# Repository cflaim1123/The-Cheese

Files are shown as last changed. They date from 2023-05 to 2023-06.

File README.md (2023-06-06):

# The-Cheese
This repository documents the design and construction of a sensor that measures changes in water clarity due to wave action.

The water clarity sensor uses image recognition analysis of ball markers at known distances from the camera to calculate visibility distance in a water column. The sensor takes pressure readings at 5 Hz and takes an image to be analyzed every 100 pressure samples. The goal of the sensor is to correlate water clarity and suspended sediment concentrations to wave intensity in coastal environments. Water clarity can impact benthic organisms who rely on visible water to navigate and hunt. Additionally, cloudy water attenuates light more quickly and can reduce primary production rates in coastal photosynthesizing organisms.

Project summary:
A current study was carried out to provide a better understanding of the effects of wave intensity on suspended sediment concentrations in coastal environments. Sediment grain disruptions, generally caused by boat traffic, increase the mortality rates of species and disrupt photosynthesis. Studying sediment disturbances alongside wave energy is important for determining possible commercial and recreational regulations surrounding marine environments. While utilizing our designed and built sensor, we predict that as the measured wave intensity increases in Puget Sound, the measured suspended sediment concentration increase as well. This is due to increased wave energy resulting in increased sediment transport based on the grain size and magnitude of the wave intensity. With our sensor, we will measure the presence of a wave through pressure readings and shifts in suspended sediment concentrations with digital camera imagery. The instrument will take a picture and readings across the pressure sensor to sense the amount of suspended sediment stirred up with the occurrence of a wave. We experienced challenges across all aspects of the instrument design; from the initially considered components and appearance to the coding process and marker programming. The sensor’s deployment site is the Mukilteo T Dock chosen for its diversity in sediment grain size and isolated location. The date for our deployment is during Memorial Day weekend; a convenient holiday associated with heavy boat traffic and recreational wave energy. Eventually, through a familiar cycle of trial and error, we were able to achieve a functional sensor known to us as The Cheese.

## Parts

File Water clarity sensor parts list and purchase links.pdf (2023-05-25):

Water clarity sensor parts list and purchase links Electronics
- Adafruit ESP32-s2 feather BME (https://www.adafruit.com/product/5303)
- AIthinker ESP32-cam (https://www.amazon.com/ESP32-CAM-MB-Aideepen-ESP32-CAM-Bluetooth-Arduino/dp/B0948ZFTQZ)
- MS5803BA_05 pressure sensor (https://www.digikey.com/en/products/detail/te-connectivity-measurement-specialties/MS580314BA01-00/5277631) on 4-pint (+3V, -3V, SDA, SCL) breakout board
- DS3231 real time clock (RTC) (https://www.amazon.com/HiLetgo-AT24C32-Arduino-Without-Battery/dp/B00LX3V7F0?hvadid=312400581241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)
- DF robot SD card module (https://www.digikey.com/en/products/detail/dfrobot/DFR0229/6588460)
- 6-pin switch (https://www.digikey.com/en/products/detail/c&k/JS202011CQN/1640097)
- 9V battery (x2) (https://www.amazon.com/AmazonBasics-Volt-Everyday-Alkaline-Battery/dp/B081FGCRQQ?hvadid=177774793098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)
- 9V battery lead wires (x2) (https://www.amazon.com/Chanzon-Battery-Connector-Plastic-Arduino/dp/B083QF1KHN)
- Female header mounts (https://www.amazon.com/Cimeton-Electrical-Connectors-Assortment-Prototype/dp/B09B92JPD3)
- Double-sided perf board (https://www.amazon.com/DEYUE-Double-sided-Prototyping-Solder-able-Protoboards/dp/B07FFDFLZ3?s=industrial)
- Multi-colored breadboard wires (https://www.amazon.com/TUOFENG-Hookup-Wires-6-Different-Colored/dp/B07TX6BX47?s=industrial)

Hardware
- Waterproof housing (https://www.polycase.com/ml-46f)
- M3 bolts (x2) (https://www.amazon.com/Assortment-Stainless-Replacement-Machine-Fastener/dp/B0BMQFHDBH?s=industrial)
- M3 lock nuts (x2) (https://www.amazon.com/100Pcs-Stainless-Self-Lock-Inserted-Clinching/dp/B075ZZW7VL?s=industrial)
- Bricks (~5 pounds) (x6) (https://www.homedepot.com/p/Basalite-8-in-x-4-in-x-2-in-Concrete-HW-Brick-Natural-100015626/316606769)
- 12” zip ties (x24) (https://www.amazon.com/White-Strength-Nylon-Bolt-Dropper/dp/B06X1CKSD2?s=industrial)
- 6” zip ties (https://www.amazon.com/KOOWIN-Small-Nylon-Plastic-Cable/dp/B08HMPBY3L?s=industrial)
- ½” plywood (~2 sq. ft) (https://www.homedepot.com/p/Handprint-Sanded-Plywood-Common-1-2-in-x-2-ft-x-4-ft-Actual-0-451-in-x-23-75-in-x-47-75-in-300896/202093833)
- 0.84” OD PVC pipe (1/2” ID) (~5m) (https://www.homedepot.com/p/Charlotte-Pipe-1-in-x-10-ft-PVC-Schedule-40-Tubing-DWV-Pipe-PVC040100600RS/100348473)
- 60° elbow connectors (x6, see project GitHub) (https://github.com/cflaim1123/The-Cheese)
- 90° elbow connectors (x8, see project GitHub) (https://github.com/cflaim1123/The-Cheese)
- Ball distance markers (x14, see project GitHub) (https://github.com/cflaim1123/The-Cheese)
- 1mm wire (~1m) (https://www.amazon.com/Hillman-Group-123106-Galvanized-Steel/dp/B000BPEQAE?hvadid=631557517645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)

Filament
- ABS filament (any color, ~1/4 spool) (https://www.amazon.com/HATCHBOX-3D-Filament-Dimensional-Accuracy/dp/B00MEZEAZ0?s=industrial)

Sealants
- Marine sealant 5200 (https://www.amazon.com/3M-5200FC-Marine-Adhesive-Sealant/dp/B003E1ULRE)
- Hot glue

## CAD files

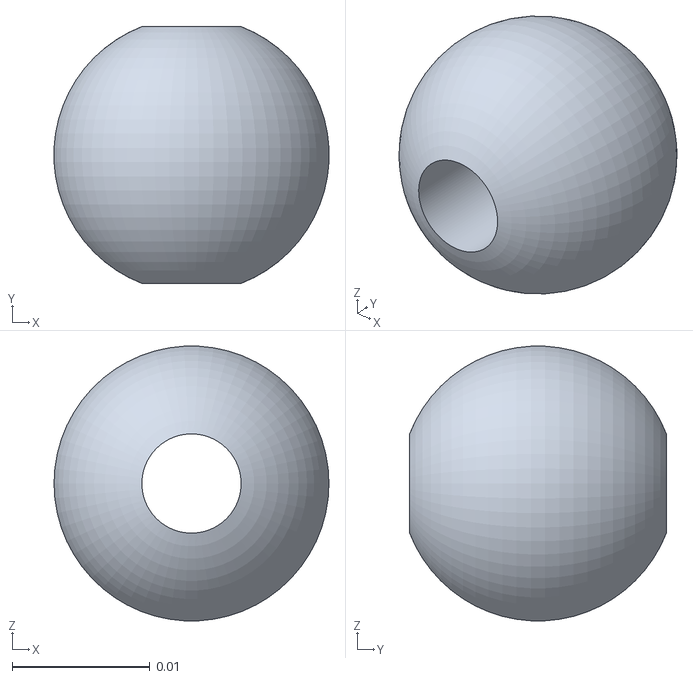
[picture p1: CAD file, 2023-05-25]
STL FILES/ballMarker.stl
0.02 x 0.0187 x 0.0199

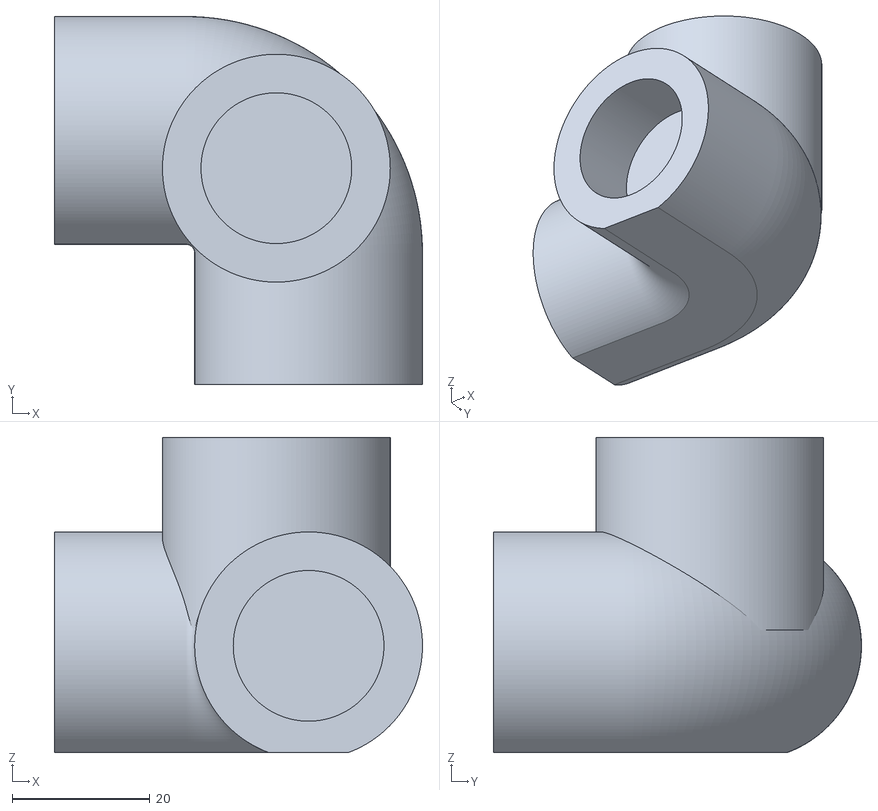
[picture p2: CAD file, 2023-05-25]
STL FILES/90deg0_84InchElbow.stl
53.3 x 53.3 x 45.7

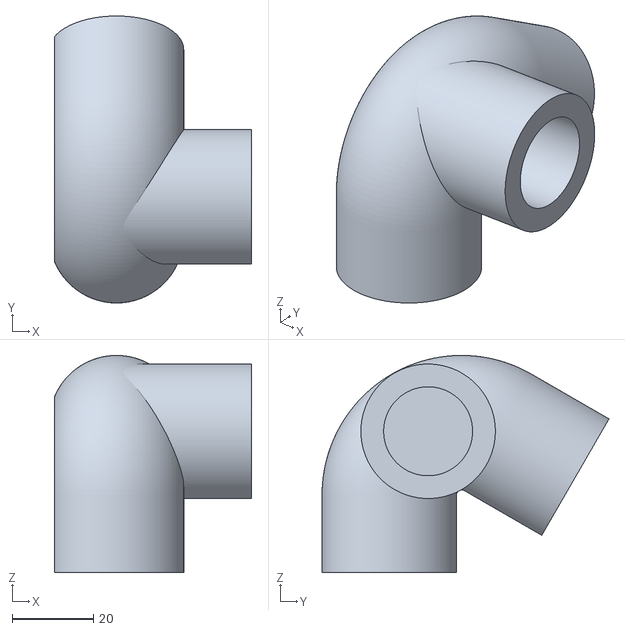
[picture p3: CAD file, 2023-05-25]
STL FILES/60Deg0_84InchElbow.stl
48.4 x 70.5 x 53.3

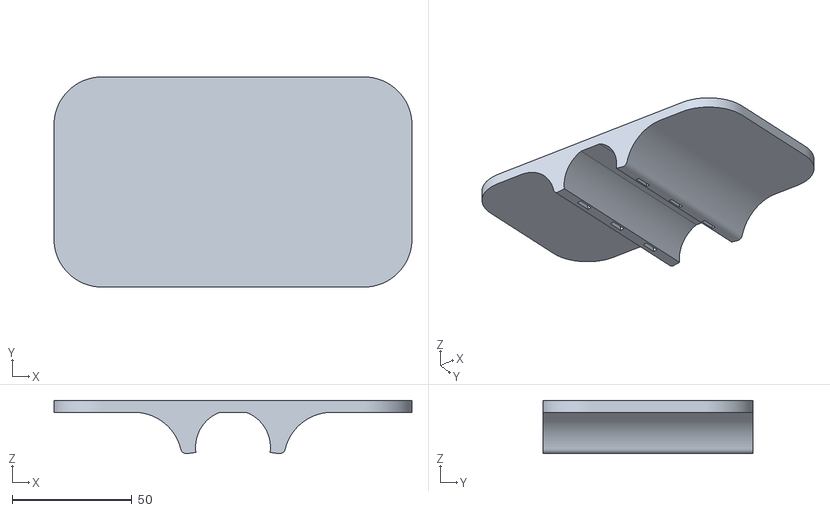
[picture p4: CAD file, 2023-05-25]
STL FILES/waterClaritySensorPipeMountV3.stl
149.3 x 87.6 x 22.2

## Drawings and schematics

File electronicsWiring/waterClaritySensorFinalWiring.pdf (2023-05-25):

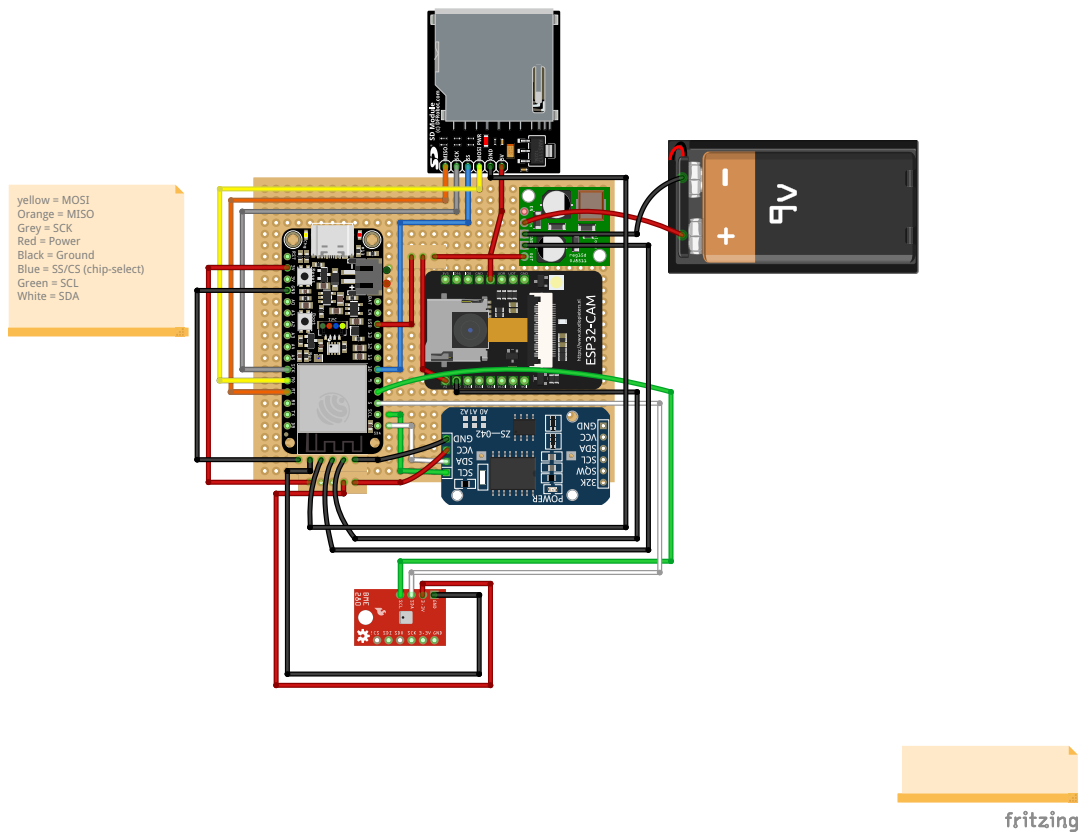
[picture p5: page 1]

yellow = MOSI
Orange = MISO
Grey = SCK
Red = Power
Black = Ground
Blue = SS/CS (chip-select)
Green = SCL
White = SDA

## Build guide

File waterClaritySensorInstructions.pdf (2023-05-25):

Water clarity sensor user instructions
1) Ensure the two 9v batteries beneath the main electronics board are near a full charge.
2) Remove the camera module and then press the SD card to remove it. Delete any photos previously saved to it. Insert the SD card back into the camera module and replace the camera into the female header pins.
3) Pull up an online clock (https://clock.zone/) with millisecond accuracy. Be prepared to take a screenshot of the time while simultaneously turning on the sensor.
4) Locate the power switch in the upper right-hand corner. Pull the switch down (towards the red wire beneath the board) at the same time as taking a screenshot of the current time. You should now see red and orange LEDs on the board.
5) House the battery pack beneath the main board and gently press the main electronics board into place. The stand-offs on the bottom should sit on either side of the two batteries. Note: the batteries will curve slightly inward due to the shape of the housing.
6) Make sure all wires are clear of the O-ring lip prior to sealing the lid onto the housing. Make sure now wires are visibility broken.
7) Gently clean the lid of the pressure casing with methanol or rubbing alcohol.
8) Place the lid onto the pressure housing and begin the tight the four corner screws in a star-like pattern. Once all the screws are loosely in place, fully tighten them. You should still see the LEDs on the board to be powered on.
9) Ensure that the screws are fully tightened and there are no gaps between the lid and pressure housing.
10) Tightly wrap 2 – 4 layers of electrical tape around the seal between the lid and pressure housing. Be sure to overlap the layers so that the tape covers ~1inch in width.
11) Firmly run your fingers over the electrical tape to ensure it has adhered to the pressure vessel.
12) Snap the sealed pressure casing the vertical leg of The Cheese beneath the mounted pressure sensor. Locate three ~6” zip ties.
13) Slide the zip ties through the holes on the back of the pipe mount piece and firmly tighten them so that the pressure housing does not easily rotate.
14) Orient the camera in the pressure housing so that it is aligned with the ball markers.
15) Carry the water clarity sensor to the sampling location along with a flotation device for surface expression. Tie the buoy to the sensor frame upon arrival.
16) Gently lower the sensor into the water and leave submerged for the desired sampling time.
17) To retrieve data from the sensor, unseal the pressure casing (follow steps 11 – 8 in reverse order) and remove the camera SD card. If there is no data on this SD card, check the backup SD card on the bottom side of the main electronics board.

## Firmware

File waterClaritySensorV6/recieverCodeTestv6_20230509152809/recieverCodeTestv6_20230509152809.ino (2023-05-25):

// Include Required Libraries
// Camera libraries
#include "esp_camera.h"
#include "soc/soc.h"
#include "soc/rtc_cntl_reg.h"
#include "driver/rtc_io.h"
// MicroSD Libraries
#include "FS.h"
#include "SD_MMC.h"
// Data transmission libraries
#include <esp_now.h>
#include <WiFi.h>

// Pin definitions for CAMERA_MODEL_AI_THINKER
#define PWDN_GPIO_NUM     32
#define RESET_GPIO_NUM    -1
#define XCLK_GPIO_NUM      0
#define SIOD_GPIO_NUM     26
#define SIOC_GPIO_NUM     27
#define Y9_GPIO_NUM       35
#define Y8_GPIO_NUM       34
#define Y7_GPIO_NUM       39
#define Y6_GPIO_NUM       36
#define Y5_GPIO_NUM       21
#define Y4_GPIO_NUM       19
#define Y3_GPIO_NUM       18
#define Y2_GPIO_NUM        5
#define VSYNC_GPIO_NUM    25
#define HREF_GPIO_NUM     23
#define PCLK_GPIO_NUM     22

// MAC Address of responder - edit as required
uint8_t broadcastAddress[] = {0x84, 0xF7, 0x03, 0xEC, 0xE5, 0x66};

typedef struct struct_message {
  char a[32];
  int b;
  float c;
  float d;
  bool e;
  unsigned long f;
} struct_message;

// Create a structured object
struct_message sensorData;

// Data file 
File dataFile;
const char fileName[] = "/data.csv";

// Counter for picture number
unsigned int pictureCount = 0;
// Delay time in millieconds
unsigned int delayTime = 2020;

// Callback function executed when data is received
void OnDataRecv(const uint8_t * mac, const uint8_t *incomingData, int len) {
  memcpy(&sensorData, incomingData, sizeof(sensorData));
  Serial.print("Data received: ");
  Serial.println(len);
  Serial.print("Time: ");
  Serial.println(sensorData.a);
  Serial.print("Sample num: ");
  Serial.println(sensorData.b);
  Serial.print("Pressure: ");
  Serial.println(sensorData.c);
  Serial.print("Temp: ");
  Serial.println(sensorData.d);
  Serial.print("Picture flag:");
  Serial.println(sensorData.e);
  Serial.print("Elapsed time: ");
  Serial.println(sensorData.f);
  Serial.println();

  String tempDataRow = String(sensorData.b) + "," + String(sensorData.c) + "," + sensorData.d + 
  "," + String(sensorData.a) + "," + String(sensorData.e) + "," + String(sensorData.f);
  const char* dataRow = tempDataRow.c_str();
  appendFile(SD_MMC, "/data.csv",dataRow);

  // Take and Save Photo
  if(sensorData.e == true){
    // Path where new image will be saved in MicroSD card
    String path = "/image_" + String(sensorData.b) +  ".jpg";
    Serial.printf("Picture file name: %s\n", path.c_str());
    takeNewPhoto(path);
  }
}
void appendFile(fs::FS &fs, const char * path, const char * message){
    Serial.printf("Appending to file: %s\n", path);

    File file = fs.open(path, FILE_APPEND);
    if(!file){
        Serial.println("Failed to open file for appending");
        return;
    }
    if(file.println(message)){
        Serial.println("Message appended");
    } else {
        Serial.println("Append failed");
    }
}

void configESPCamera() {
// Configure Camera parameters
// Object to store the camera configuration parameters
camera_config_t config;
config.ledc_channel = LEDC_CHANNEL_0;
config.ledc_timer = LEDC_TIMER_0;
config.pin_d0 = Y2_GPIO_NUM;
config.pin_d1 = Y3_GPIO_NUM;
config.pin_d2 = Y4_GPIO_NUM;
config.pin_d3 = Y5_GPIO_NUM;
config.pin_d4 = Y6_GPIO_NUM;
config.pin_d5 = Y7_GPIO_NUM;
config.pin_d6 = Y8_GPIO_NUM;
config.pin_d7 = Y9_GPIO_NUM;
config.pin_xclk = XCLK_GPIO_NUM;
config.pin_pclk = PCLK_GPIO_NUM;
config.pin_vsync = VSYNC_GPIO_NUM;
config.pin_href = HREF_GPIO_NUM;
config.pin_sscb_sda = SIOD_GPIO_NUM;
config.pin_sscb_scl = SIOC_GPIO_NUM;
config.pin_pwdn = PWDN_GPIO_NUM;
config.pin_reset = RESET_GPIO_NUM;
config.xclk_freq_hz = 20000000;
config.pixel_format = PIXFORMAT_JPEG; // Choices are YUV422, GRAYSCALE, RGB565, JPEG
// Select lower framesize if the camera doesn't support PSRAM
if (psramFound()) {
  config.frame_size = FRAMESIZE_VGA; // FRAMESIZE_ + QVGA|CIF|VGA|SVGA|XGA|SXGA|UXGA
  config.jpeg_quality = 10; //10-63 lower number means higher quality
  config.fb_count = 2;
} else {
  config.frame_size = FRAMESIZE_SVGA;
  config.jpeg_quality = 12;
  config.fb_count = 1;
}
// Initialize the Camera
esp_err_t err = esp_camera_init(&config);
if (err != ESP_OK) {
  Serial.printf("Camera init failed with error 0x%x", err);
  return;
}
// Camera quality adjustments
sensor_t * s = esp_camera_sensor_get();
// BRIGHTNESS (-2 to 2)
s->set_brightness(s, 1);
// CONTRAST (-2 to 2)
s->set_contrast(s, 0);
// SATURATION (-2 to 2)
s->set_saturation(s, 0);
// SPECIAL EFFECTS (0 - No Effect, 1 - Negative, 2 - Grayscale, 3 - Red Tint, 4 - Green Tint, 5 - Blue Tint, 6 - Sepia)
s->set_special_effect(s, 0);
// WHITE BALANCE (0 = Disable , 1 = Enable)
s->set_whitebal(s, 1);
// AWB GAIN (0 = Disable , 1 = Enable)
s->set_awb_gain(s, 1);
// WB MODES (0 - Auto, 1 - Sunny, 2 - Cloudy, 3 - Office, 4 - Home)
s->set_wb_mode(s, 0);
// EXPOSURE CONTROLS (0 = Disable , 1 = Enable)
s->set_exposure_ctrl(s, 1);
// AEC2 (0 = Disable , 1 = Enable)
s->set_aec2(s, 0);
// AE LEVELS (-2 to 2)
s->set_ae_level(s, 0);
// AEC VALUES (0 to 1200)
s->set_aec_value(s, 300);
// GAIN CONTROLS (0 = Disable , 1 = Enable)
s->set_gain_ctrl(s, 1);
// AGC GAIN (0 to 30)
s->set_agc_gain(s, 0);
// GAIN CEILING (0 to 6)
s->set_gainceiling(s, (gainceiling_t)0);
// BPC (0 = Disable , 1 = Enable)
s->set_bpc(s, 0);
// WPC (0 = Disable , 1 = Enable)
s->set_wpc(s, 1);
// RAW GMA (0 = Disable , 1 = Enable)
s->set_raw_gma(s, 1);
// LENC (0 = Disable , 1 = Enable)
s->set_lenc(s, 1);
// HORIZ MIRROR (0 = Disable , 1 = Enable)
s->set_hmirror(s, 0);
// VERT FLIP (0 = Disable , 1 = Enable)
s->set_vflip(s, 0);
// DCW (0 = Disable , 1 = Enable)
s->set_dcw(s, 1);
// COLOR BAR PATTERN (0 = Disable , 1 = Enable)
s->set_colorbar(s, 0);
}

// Camera Flashes every time the SD card is accessed
// void initMicroSDCard() {
//  // Start the MicroSD card
//  Serial.println("Mounting MicroSD Card");
//  if (!SD_MMC.begin()) {
//    Serial.println("MicroSD Card Mount Failed");
//    return;
//  }
// }

// Camera does not flash everytime the SD card is used
void initMicroSDCard() {
 // Start the MicroSD card
 Serial.println("Mounting MicroSD Card");
 if (!SD_MMC.begin("/sdcard", true)) {
   Serial.println("MicroSD Card Mount Failed");
   return;
 }
 uint8_t cardType = SD_MMC.cardType();
 if (cardType == CARD_NONE) {
   Serial.println("No MicroSD Card found");
   return;
 }
}


void takeNewPhoto(String path) {
// Take Picture with Camera
// Setup frame buffer
camera_fb_t  * fb = esp_camera_fb_get();
if (!fb) {
  Serial.println("Camera capture failed");
  return;
}
// Save picture to microSD card
fs::FS &fs = SD_MMC;
File file = fs.open(path.c_str(), FILE_WRITE);
if (!file) {
  Serial.println("Failed to open file in write mode");
}
else {
  file.write(fb->buf, fb->len); // payload (image), payload length
  Serial.printf("Saved file to path: %s\n", path.c_str());
}
// Close the file
file.close();
// Return the frame buffer back to the driver for reuse
esp_camera_fb_return(fb);
}

void writeToDataFile(String data)
{
  dataFile = SD_MMC.open(fileName, FILE_WRITE);
  //dataFile.seek(EOF);
  //fs::FS &fs = SD_MMC;
  //dataFile = fs.open(fileName, FILE_WRITE);
  if (dataFile) // it opened OK
    {
    Serial.println("Writing to dataFile.csv");
    dataFile.println(data);
    dataFile.close(); 
    Serial.println("Done");
    }
  else 
    Serial.println("Error opening data.csv");
}

void setup() {
  // Disable brownout detector
  WRITE_PERI_REG(RTC_CNTL_BROWN_OUT_REG, 0);
  // Start Serial Monitor
  Serial.begin(115200);
  // Set ESP32 as a Wi-Fi Station
  WiFi.mode(WIFI_STA);


  // Initilize ESP-NOW
  if (esp_now_init() != ESP_OK) {
    Serial.println("Error initializing ESP-NOW");
    return;
  }

  // Register callback function
  esp_now_register_recv_cb(OnDataRecv);

  // Initialize the camera
  Serial.print("Initializing the camera module...");
  configESPCamera();
  Serial.println("Camera OK!");
  // Initialize the MicroSD
  Serial.print("Initializing the MicroSD card module... ");
  initMicroSDCard();
  Serial.print("Delay Time = ");
  Serial.print(delayTime);
  Serial.println(" ms");

  dataFile = SD_MMC.open(fileName, FILE_WRITE);
  String tempHeader = "Sample #, Pressure (mbar), Temperature (deg C), Time (yyyy-MM-dd HH:mm:ss), Picture sample (T/F), Elapsed time since power on";
  const char* header = tempHeader.c_str();
  //fs::FS &fs = SD_MMC;
  //dataFile = fs.open(fileName, FILE_WRITE);
  if (dataFile) // it opened OK
    {
    Serial.println("Writing to dataFile.csv");
    dataFile.println(header);
    dataFile.close(); 
    Serial.println("Done");
    }
}

void loop() {
}

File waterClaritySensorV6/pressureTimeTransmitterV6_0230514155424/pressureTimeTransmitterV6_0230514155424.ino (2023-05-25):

// Include Libraries
#include <esp_now.h>
#include <WiFi.h>
#include <Wire.h>
#include "RTClib.h"
#include <MS5803_05.h> 
#include "FS.h"
#include "SD.h"
#include "SPI.h"

#define I2C_BUS_1_SDA 6 
#define I2C_BUS_1_SCL 9 
#define chipSelect 10

// Make datetime variable
char buffer[] = "yyyy-MM-dd HH:mm:ss";

// Make second I2C bus
TwoWire bus1 = TwoWire(1);

// Initialize clock and pressure sensor objects
MS_5803 press1 = MS_5803(512, &bus1, I2C_BUS_1_SDA, I2C_BUS_1_SCL);
RTC_DS3231 rtc;

// Variables for test data
int sample_num = 0;
float pressure;
float temp; 
bool picture_flag = true;
bool sleep_flag = false;

// Sample number tracker for picture flag
int last_picture_sample = 0;
unsigned long elapsed_time = 0;

// Serial communication baud rate
int baud = 115200;
int sample_delay = 1000;
unsigned long elapsed_time_at_sample;

// MAC Address of responder
uint8_t broadcastAddress[] = {0xCC, 0xDB, 0xA7, 0xE64, 0x58, 0x48}; 

// Define a data structure
typedef struct struct_message {
  char a[32];
  int b;
  float c;
  float d;
  bool e;
  unsigned long f;
} struct_message;

// Create a structured object
struct_message sensorData;

// Peer info
esp_now_peer_info_t peerInfo;

void setup() {
  Serial.begin(baud);
  unsigned long start = millis();
  Serial.print("Time millis:");
  Serial.println(start);
  Serial.println();
  Serial.println();
  Wire.begin();
  rtc.begin();
  delay(500);

  // initialize SD card
  initMicroSDCard();
  // initialize pressure sensor
  initPressureSensor();
  // initialize RTC
  initRTC();
  // initialize ESP Now and peer address info
  initESPNow();

  // Uncomment the following line to set the time
  rtc.adjust(DateTime(F(__DATE__), F(__TIME__)));

  DateTime now = rtc.now();
  String nowString = String(now.year()) + "-" + String(now.month()) + "-" + 
  String(now.day()) + " " + String(now.hour()) + ":" + String(now.minute()) + ":" + String(now.second());

  String tempHeader = "################## Metadata log start ##################";
  const char* logHeader = tempHeader.c_str();
  logFile(SD, logHeader, true);

  tempHeader = "Sample #, Pressure (mbar), Temperature (deg C), Time (yyyy-MM-dd HH:mm:ss), Picture sample (T/F), Elapsed time since power on";
  const char* header = tempHeader.c_str();
  appendFile(SD, "/data.csv", header);
}

void loop() {
  String sampleString = "Sample: " + String(sample_num);
  logFile(SD, sampleString.c_str(), true);

  // Get current time, pressure, and temp
  DateTime now = rtc.now();
  press1.readSensor();
  pressure = press1.pressure();
  temp = press1.temperature();
  elapsed_time_at_sample = millis();
  delay(10);

  if(pressure > 1020){
    sample_delay = 200;
  }

  String nowString = String(now.year()) + "-" + String(now.month()) + "-" + String(now.day()) + 
  " " + String(now.hour()) + ":" + String(now.minute()) + ":" + String(now.second());
  delay(10);

  // Set default pressure flag
  picture_flag = false;
  // Set picture flag
  if(sample_num % 100 == 0){
      picture_flag = true;
  }
  
  
  // Format structured data
   strcpy(sensorData.a, nowString.c_str());
  sensorData.b = sample_num;
  sensorData.c = pressure;
  sensorData.d = temp;
  sensorData.e = picture_flag;
  sensorData.f = elapsed_time_at_sample;

  // Create data row and write it to file
  String tempDataRow = String(sample_num) + "," + String(pressure) + "," + String(temp) + "," + 
      nowString + "," + String(picture_flag) + "," + String(elapsed_time_at_sample);
  const char* dataRow = tempDataRow.c_str();
  //Serial.println("Created data row");

  appendFile(SD, "/data.csv", dataRow);

    // Send message via ESP-NOW
  esp_err_t result = esp_now_send(broadcastAddress, (uint8_t *) &sensorData, sizeof(sensorData));
   
  if (result == ESP_OK) {
    Serial.println("Sending confirmed");
    logFile(SD, "Sending confirmed", true);
    logFile(SD, "", true);
  }
  else {
    Serial.println("Sending error");
    logFile(SD, "Sending error", true);
    logFile(SD, "", true);
  }
    // Print sent data to serial monitor
  Serial.print("pressure: ");
  Serial.println(pressure);
  Serial.print("Temperature: ");
  Serial.println(temp);
  Serial.print("Date and time:");
  //Serial.println(nowString);

  Serial.print(now.year());
  Serial.print('/');
  Serial.print(now.month(), DEC);
  Serial.print('/');
  Serial.print(now.day(), DEC);
  Serial.print(" ");
  //Serial.print(daysOfTheWeek[now.dayOfTheWeek()]);
  //Serial.print(") ");
  Serial.print(now.hour(), DEC);
  Serial.print(':');
  Serial.print(now.minute(), DEC);
  Serial.print(':');
  Serial.print(now.second(), DEC);
  Serial.println();

  sample_num++;
  delay(sample_delay); 
}

//_____________________________________________________________________________________//
// Init                                                                                //
//_____________________________________________________________________________________//

void initESPNow(){
// Set ESP32 as a Wi-Fi Station
  WiFi.mode(WIFI_STA);

  // Initilize ESP-NOW
  if (esp_now_init() != ESP_OK) {
    Serial.println("Error initializing ESP-NOW");
    logFile(SD, "Error initializing ESP-NOW", true);
    return;
  }

  delay(1000);

  // Register the send callback
  esp_now_register_send_cb(OnDataSent);

  delay(1000);
  
  // Register peer
  memcpy(peerInfo.peer_addr, broadcastAddress, 6);
  peerInfo.channel = 0;  
  peerInfo.encrypt = false;
  delay(1000);

  // Add peer        
  if (esp_now_add_peer(&peerInfo) != ESP_OK){
    Serial.println("Failed to add peer");
    logFile(SD, "Failed to add peer", true);
    return;
  }
  delay(1000);
}

void initRTC(){
  if (! rtc.begin()) {
    Serial.println("Couldn't find RTC");
    logFile(SD, "Couldn't find RTC", true);
    Serial.flush();
    //while (1) delay(10);
  }

  if (rtc.lostPower()) {
    Serial.println("RTC lost power, let's set the time!");
    logFile(SD, "RTC lost power, let's set the time!", true);
    // When time needs to be set on a new device, or after a power loss, the
    // following line sets the RTC to the date & time this sketch was compiled
    rtc.adjust(DateTime(F(__DATE__), F(__TIME__)));
    // This line sets the RTC with an explicit date & time, for example to set
    // January 21, 2014 at 3am you would call:
    // rtc.adjust(DateTime(2014, 1, 21, 3, 0, 0));
  }
}
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
